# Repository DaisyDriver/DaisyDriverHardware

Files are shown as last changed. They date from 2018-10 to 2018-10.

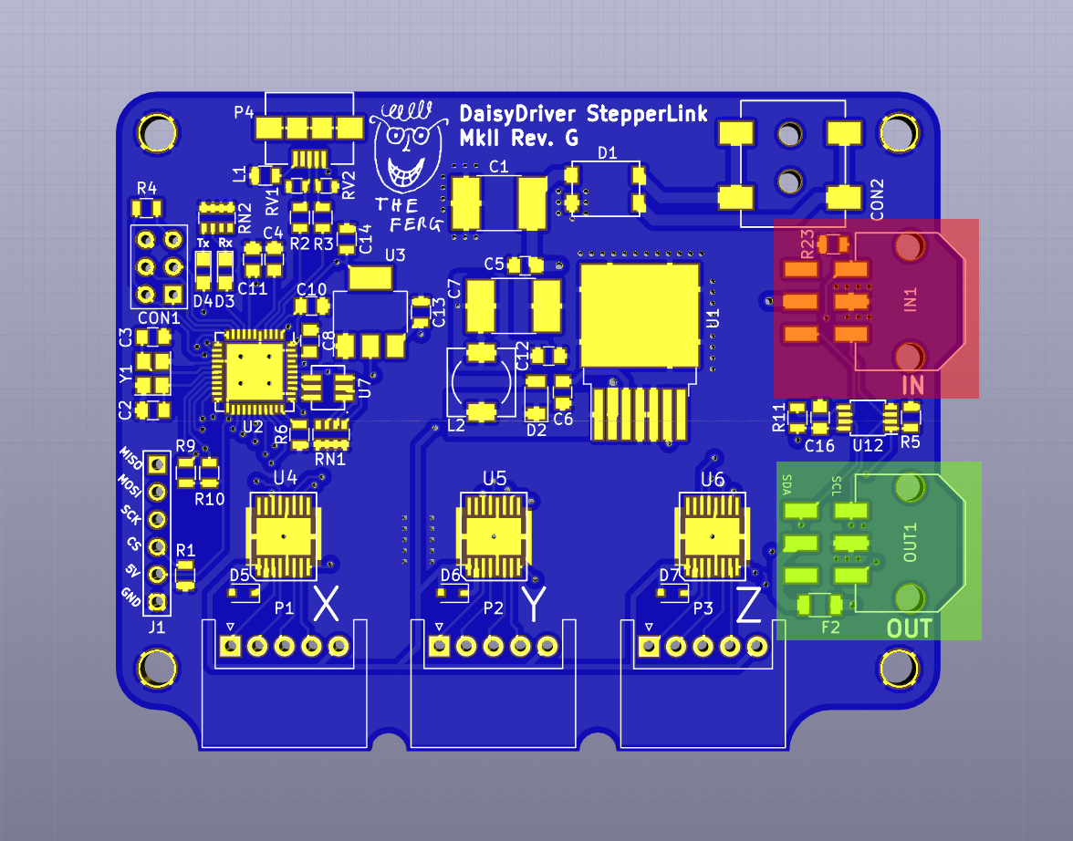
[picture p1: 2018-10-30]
board features/board_CAD_input_output.png

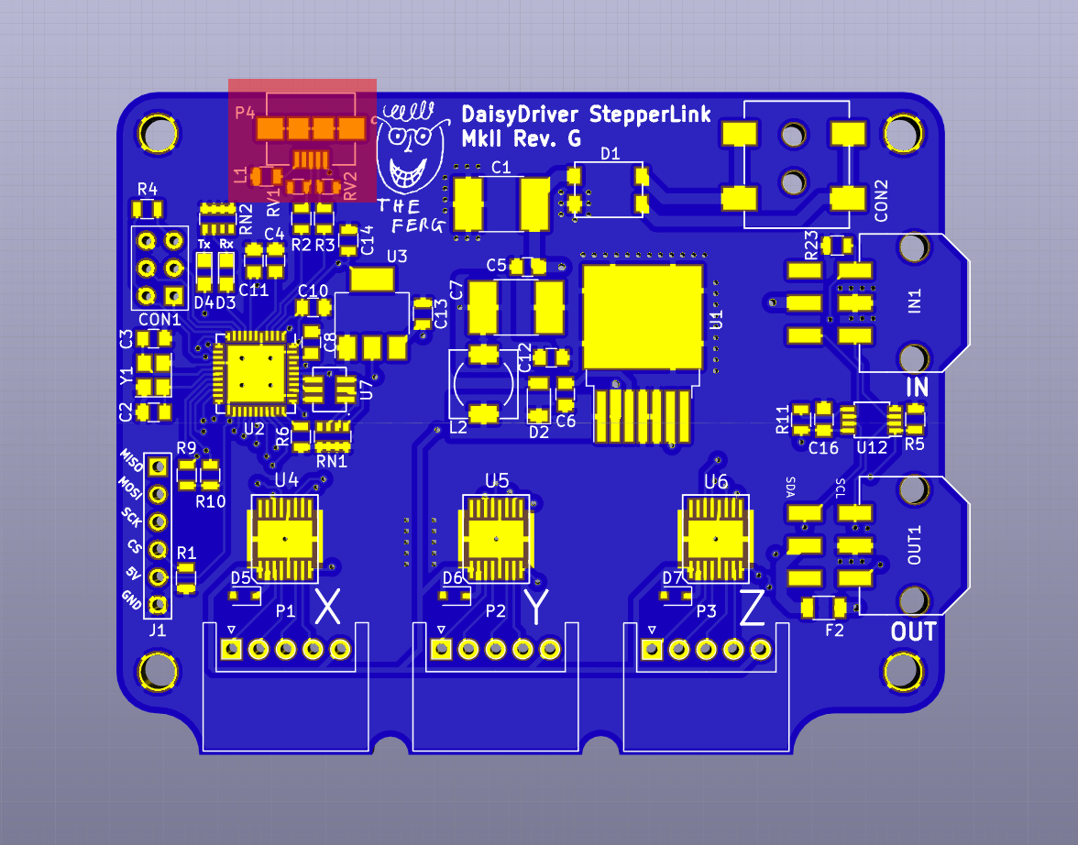
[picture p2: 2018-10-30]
board features/board_CAD_USB.png

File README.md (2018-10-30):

# DaisyDriver
The DaisyDriver project aims to make automation a common feature of scientific experiments by providing scientists with a simple, powerful interface to control motors in their setups. The [wiki](https://github.com/fr293/DaisyDriver/wiki/Getting-Started) contains information on how DaisyDrivers are assembled, programmed and operated.

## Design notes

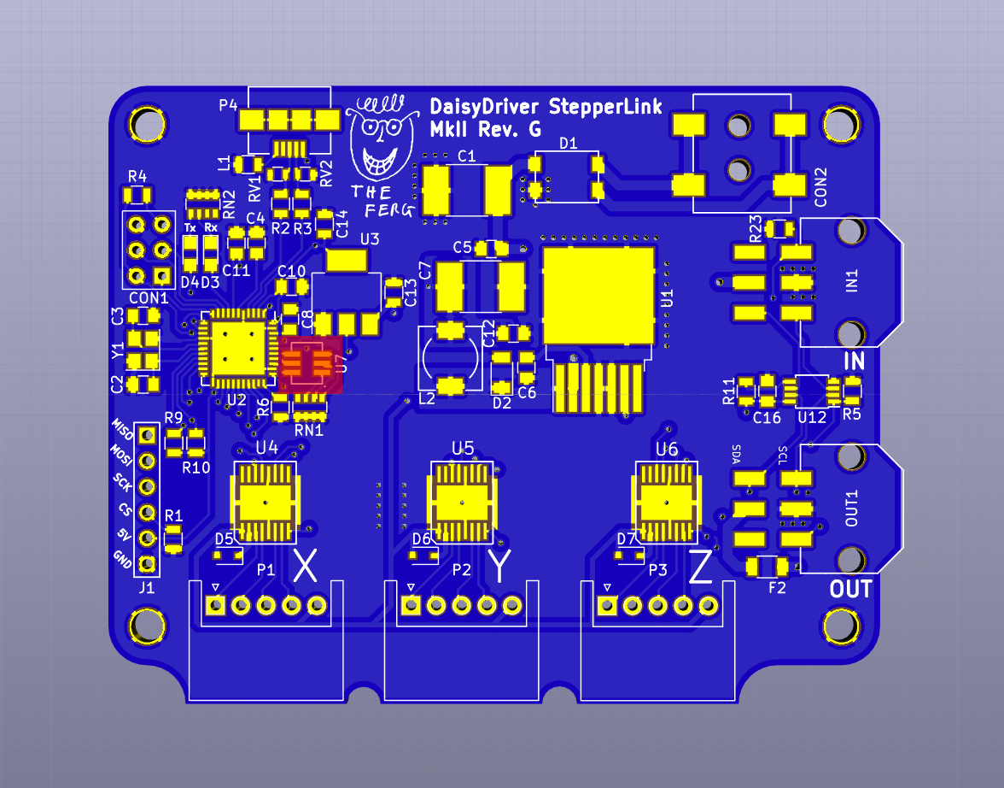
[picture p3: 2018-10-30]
board features/board_CAD_status_LED.png

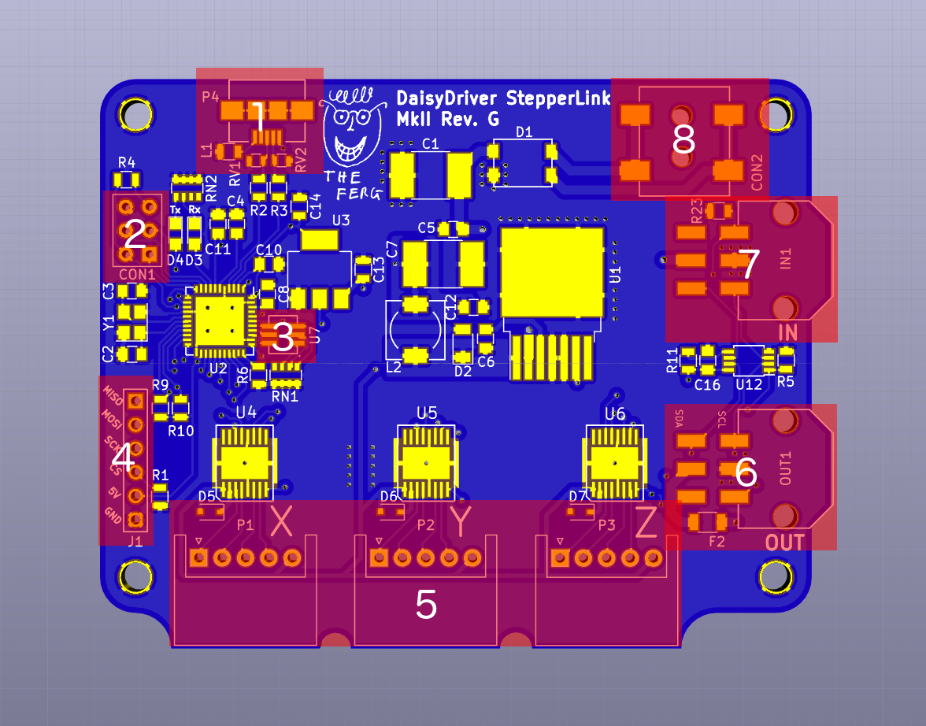
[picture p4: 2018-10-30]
board features/board_CAD_numbered_features.png

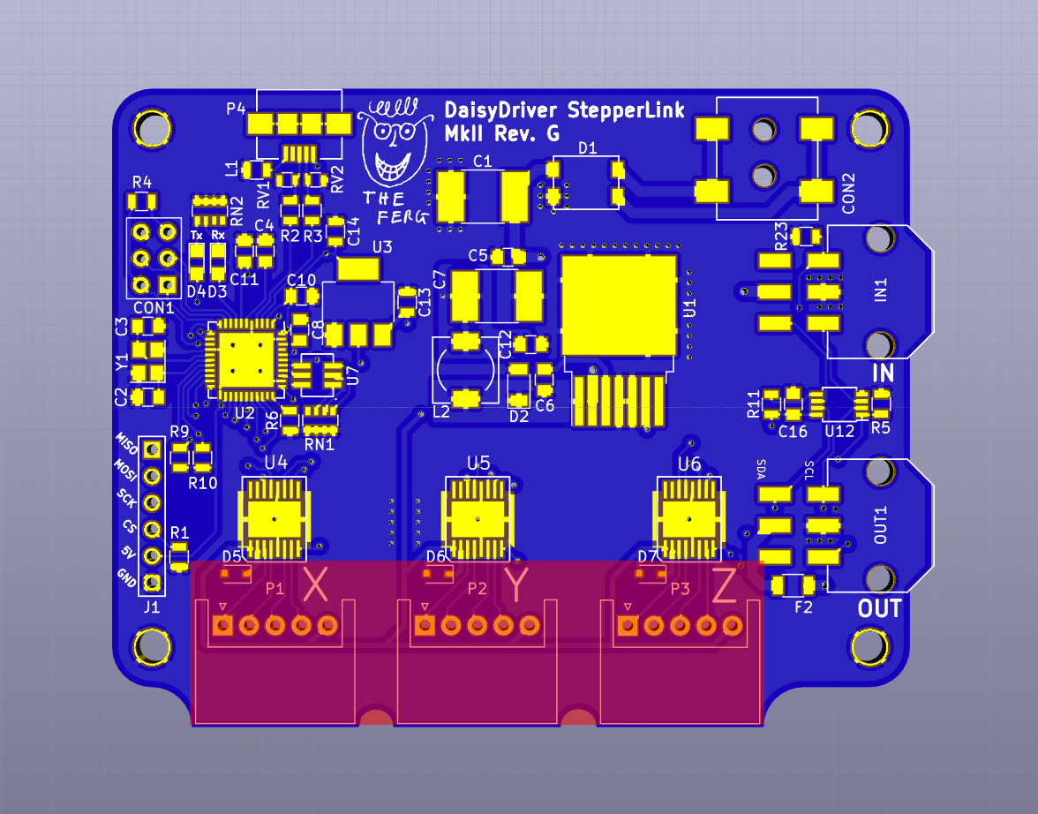
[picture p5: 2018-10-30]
board features/board_CAD_motors.png

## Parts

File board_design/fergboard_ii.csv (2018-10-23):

Id | Designator | Package | Quantity | Designation | Supplier and ref
1 | CON2 | SMD_Jack | 1 | BARREL_JACK
2 | L2 | Choke_SMD_6.3x6.3_H3 | 1 | 33u
3 | C2,C3 | C_0805 | 2 | 18p
4 | C4,C9,C12 | C_0805 | 3 | 1u
5 | C5,C10,C8,C11,C16 | C_0805 | 5 | 100n
6 | C6 | C_0805 | 1 | 10n
7 | CON1 | SW_NKK_G1xJP | 1 | AVR-ISP-6
8 | R2,R3 | R_0805 | 2 | 22
9 | R4,R9,R10,R23,R6,R11,R5,R13 | R_0805 | 8 | 10k
10 | RV2,RV1 | R_0603 | 2 | Varistor_[CG0603MLC-05E_Bourns]
11 | U2 | QFN-44-1EP_7x7mm_Pitch0.5mm | 1 | ATMEGA16U4-M-pad-connected
12 | U3 | SOT-223 | 1 | lm1117
13 | U4,U5,U6 | DRV8805 | 3 | DRV8805
14 | P4 | USB_Micro_B | 1 | USB_OTG
15 | Y1 | Crystal_SMD_3225-4pin_3.2x2.5mm | 1 | 16M_crystal
16 | F2 | R_1206 | 1 | 2A_Polyfuse
17 | F3,F4,F5 | R_1206 | 3 | 0A125_Polyfuse
18 | D2 | D_1206 | 1 | D_Schottky_0V7
19 | RN1 | R_Array_Convex_4x0603 | 1 | 1k
20 | C1 | R_2816 | 1 | 33u
21 | C7 | R_2816 | 1 | 330u
22 | D3,D4 | LED_0805 | 2 | Yellow
23 | F1 | R_1206 | 1 | 0A5_Polyfuse
24 | R7,R8 | R_0805 | 2 | 150
25 | D1 | CD-HD2004 | 1 | D_Bridge_+-AA
26 | U7 | RGB_LED | 1 | RGB_LED
27 | L1 | R_0805 | 1 | Ferrite_Bead
28 | D5,D6,D7 | D_SOD-323 | 3 | D_Zener
29 | C13 | R_2816 | 1 | 100u
30 | IN1,OUT1 | molex_micro_fit_3_by_2_right_angle | 2 | Molex_micro_fit_3*2
31 | U8,U9,U10,U11 | 3.1_hole | 4 | hole
32 | U1 | TO-263-7_TabPin8 | 1 | lm2676_TO-263
33 | C14 | R_0805 | 1 | 10u
34 | R1 | R_0805 | 1 | 1r
35 | U12 | TSSOP-8_4.4x3mm_Pitch0.65mm | 1 | PCA9511A
36 | U13 | ferg_graphic | 1 | ferg_logo
37 | U14 | SOT-553 | 1 | NL17SZ126
38 | P1,P2,P3 | JST_XH_S05B-XH-A_05x2.50mm_Angled | 3 | CONN_01X05
39 | R12 | R_0805 | 1 | 0R

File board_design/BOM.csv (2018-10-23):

Part Number | Quantity | Description | Number of unique parts
197671 | 10 | C1 | 37
1759194 | 10 | C2
1759194 | 10 | C3
2094043 | 10 | C4
7569564 | 10 | C5
2581081 | 10 | C6
2728631 | 10 | C7
7569564 | 10 | C8
1845748 | 10 | C9
7569564 | 10 | C10
7569564 | 10 | C11
1845748 | 10 | C12
2321230 | 10 | C13
2547035 | 10 | C14
7569564 | 10 | C16
1889309 | 10 | CON2
2676044 | 10 | D1
2400198 | 10 | D2
2099227 | 10 | D3
2099227 | 10 | D4
1431198 | 10 | D5
1431198 | 10 | D6
1431198 | 10 | D7
1596993 | 10 | F1
1596993 | 10 | F2
1596988 | 10 | F3
1596988 | 10 | F4
1596988 | 10 | F5
2781934 | 10 | IN1
1669753 | 10 | L1
2667912 | 10 | L2
2781934 | 10 | OUT1
1516293 | 10 | P1
1516293 | 10 | P2
1516293 | 10 | P3
2554978 | 10 | P4
2616757 | 10 | R1
1652962 | 10 | R2
1652962 | 10 | R3
2502671 | 10 | R5
2502671 | 10 | R4
2502671 | 10 | R6
1469877 | 10 | R7
1469877 | 10 | R8
2502671 | 10 | R9
2502671 | 10 | R10
2502671 | 10 | R11
2668292 | 10 | R12
2502671 | 10 | R13
2502671 | 10 | R23
2060100 | 10 | RN1
2060166 | 10 | RV1
1838966 | 10 | RV2
1469212 | 10 | U1
2425127 | 10 | U2
2323581 | 10 | U3
2099903 | 10 | U4
2099903 | 10 | U5
2099903 | 10 | U6
2368161 | 10 | U7
2212059 | 10 | U12
2342399 | 10 | U14
1611819 | 10 | Y1
2723776 | 10 | Cables
149968 | 1 | Solder paste

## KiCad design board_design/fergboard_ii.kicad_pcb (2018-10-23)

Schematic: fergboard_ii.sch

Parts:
C1: 33u; R_2816
C2, C3: 18p; C_0805
C4, C12: 1u; C_0805
C5, C8, C10, C11, C16: 100n; C_0805
C6: 10n; C_0805
C7: 330u; R_2816
C13, C14: 10u; R_0805
CON1: AVR-ISP-6; SW_NKK_G1xJP
CON2: BARREL_JACK; SMD_Jack
D1: D_Bridge_+-AA; CD-HD2004
D2: D_Schottky_0V7; D_1206
D3, D4: Yellow; LED_0805
D5, D6, D7: D_Zener; D_SOD-323
F2: 2A_Polyfuse; R_1206
IN1: Molex_micro_fit_3*2; molex_micro_fit_3_by_2_right_angle
J1: Conn_01x06; 1by6_connector
L1: Ferrite_Bead; R_0805
L2: 33u; Choke_SMD_6.3x6.3_H3
OUT1: Molex_micro_fit_3*2; molex_micro_fit_3_by_2_right_angle
P1, P2, P3: CONN_01X05; JST_XH_S05B-XH-A_05x2.50mm_Angled
P4: USB_OTG; USB_Micro_B
R1, R4, R5, R6, R9, R10, R11, R23: 10k; R_0805
R2, R3: 22; R_0805
RN1, RN2: 4k7; R_Array_Convex_4x0603
RV1, RV2: Varistor_[CG0603MLC-05E_Bourns]; R_0603
U1: lm2676_TO-263; TO-263-7_TabPin8
U2: ATMEGA16U4-M-pad-connected; QFN-44-1EP_7x7mm_Pitch0.5mm
U3: lm1117; SOT-223
U4, U5, U6: DRV8805
U7: RGB_LED
U8, U9, U10, U11: hole; 3.1_hole
U12: PCA9511A; TSSOP-8_3x3mm_Pitch0.65mm
U13: ferg_logo; LOGO
Y1: 16M_crystal; Crystal_SMD_3225-4pin_3.2x2.5mm

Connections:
1W_in: IN1.1 (Power_(misc)), R23.2, U2.40 ((ADC1)PF1)
1W_out: OUT1.3 (Misc_(Power)), U2.39 ((ADC4/TCK)PF4)
BLUE: U2.36 ((ADC7/TDI)PF7), U7.6 (BLUE_A)
CATCH_DIODE: C6.1, D2.1, L2.1, U1.1 (switch_output)
CONNECT_INPUTS: R5.2, U2.28 ((ADC11/PCINT4)PB4), U12.1
CS: J1.4, R1.2, U2.21 ((TXD/INT3)PD3)
D+: P4.3 (D+), R2.1, RV1.1
D-: P4.2 (D-), R3.1, RV2.1
DIRX: U2.12 ((OC0A/OC1C/~RTS~/PCINT7)PB7), U4.13 (DIR)
DIRY: U2.26 ((T1/~OC4D~/ADC9)PD6), U5.13 (DIR)
DIRZ: U2.27 ((T0/OC4D/ADC10)PD7), U6.13 (DIR)
ENABLE_MOTORS: U2.20 ((RXD/INT2)PD2), U4.8 (nENBL), U5.8 (nENBL), U6.8 (nENBL)
GREEN: U2.37 ((ADC6/TDO)PF6), U7.5 (GREEN_A)
MCU_POWER: C10.1, C14.1, C16.2, CON1.6, J1.5, R4.2, R9.2, R10.2, R11.1, U2.2 (UVCC), U2.14 (VCC), U2.24 (AVCC), U2.34 (VCC), U2.44 (AVCC), U3.2 (OUTPUT), U3.4 (OUTPUT), U12.8
MID_POWER_12V: C7.1, C12.1, C13.2, D5.2, D6.2, D7.2, L2.2, P1.5, P2.5, P3.5, U1.6 (FB), U3.3 (INPUT), U4.1 (VM), U5.1 (VM), U6.1 (VM)
MISO: CON1.1, J1.1, U2.11 ((PDO/MISO/PCINT3)PB3)
MOSI: CON1.5, J1.2, U2.10 ((PDI/MOSI/PCINT2)PB2)
unnamed: C2.1, U2.17 (XTAL1), Y1.1
unnamed: C3.1, U2.16 (XTAL2), Y1.3
unnamed: C4.1, U2.6 (UCAP)
unnamed: C6.2, U1.3 (CB)
unnamed: C8.1, U2.42 (AREF)
unnamed: CON2.1, D1.3
unnamed: CON2.2, CON2.3, D1.4
unnamed: D3.1, RN2.2
unnamed: D4.1, RN2.1
unnamed: D5.1, U4.2 (VCLAMP)
unnamed: D6.1, U5.2 (VCLAMP)
unnamed: D7.1, U6.2 (VCLAMP)
unnamed: F2.1, OUT1.5 (SCL)
unnamed: L1.1, P4.5 (GND)
unnamed: P1.1, U4.3 (OUT1)
unnamed: P1.2, U4.4 (OUT2)
unnamed: P1.3, U4.6 (OUT3)
unnamed: P1.4, U4.7 (OUT4)
unnamed: P2.1, U5.3 (OUT1)
unnamed: P2.2, U5.4 (OUT2)
unnamed: P2.3, U5.6 (OUT3)
unnamed: P2.4, U5.7 (OUT4)
unnamed: P3.1, U6.3 (OUT1)
unnamed: P3.2, U6.4 (OUT2)
unnamed: P3.3, U6.6 (OUT3)
unnamed: P3.4, U6.7 (OUT4)
unnamed: R2.2, U2.4 (D+)
unnamed: R3.2, U2.3 (D-)
unnamed: R6.2, U2.33 ((~HWB~)PE2)
unnamed: R11.2, U12.5
unnamed: RN1.1, U7.3 (RED_C)
unnamed: RN1.2, U7.2 (GREEN_C)
unnamed: RN1.3, U7.1 (BLUE_C)
POWER_IN_24V: C1.1, C5.1, D1.1 (+), F2.2, IN1.5 (SCL), U1.2 (Input)
RED: U2.38 ((ADC5/TMS)PF5), U7.4 (RED_A)
RST: CON1.3, R4.1, U2.13 (~RESET~)
RXLED: D3.2, U2.8 ((SS/PCINT0)PB0)
SCK: CON1.2, J1.3, U2.9 ((SCLK/PCINT1)PB1)
SCL: OUT1.1 (Power_(misc)), R9.1, U2.18 ((OC0B/SCL/INT0)PD0), U12.2
SCL_IN: IN1.3 (Misc_(Power)), U12.3
SDA: OUT1.4 (SDA_(1-wire)), R10.1, U2.19 ((SDA/INT1)PD1), U12.7
SDA_IN: IN1.6 (1-wire_(SDA)), U12.6
SM0: U2.30 ((ADC13/OC1B/OC4B/PCINT13)PB6), U4.11 (SM0), U5.11 (SM0), U6.11 (SM0)
SM1: U2.29 ((ADC12/OC1A/~OC4B~/PCINT12)PB5), U4.10 (SM1), U5.10 (SM1), U6.10 (SM1)
STEPX: U2.31 ((OC3A/~OC4A~)PC6), U4.14 (STEP)
STEPY: U2.25 ((ICP2/ADC8)PD4), U5.14 (STEP)
STEPZ: U2.1 ((INT6/AIN0)PE6), U6.14 (STEP)
TXLED: D4.2, U2.22 ((XCK1/~CTS~)PD5)
VBUS: C11.1, P4.1 (VBUS), U2.7 (VBUS)

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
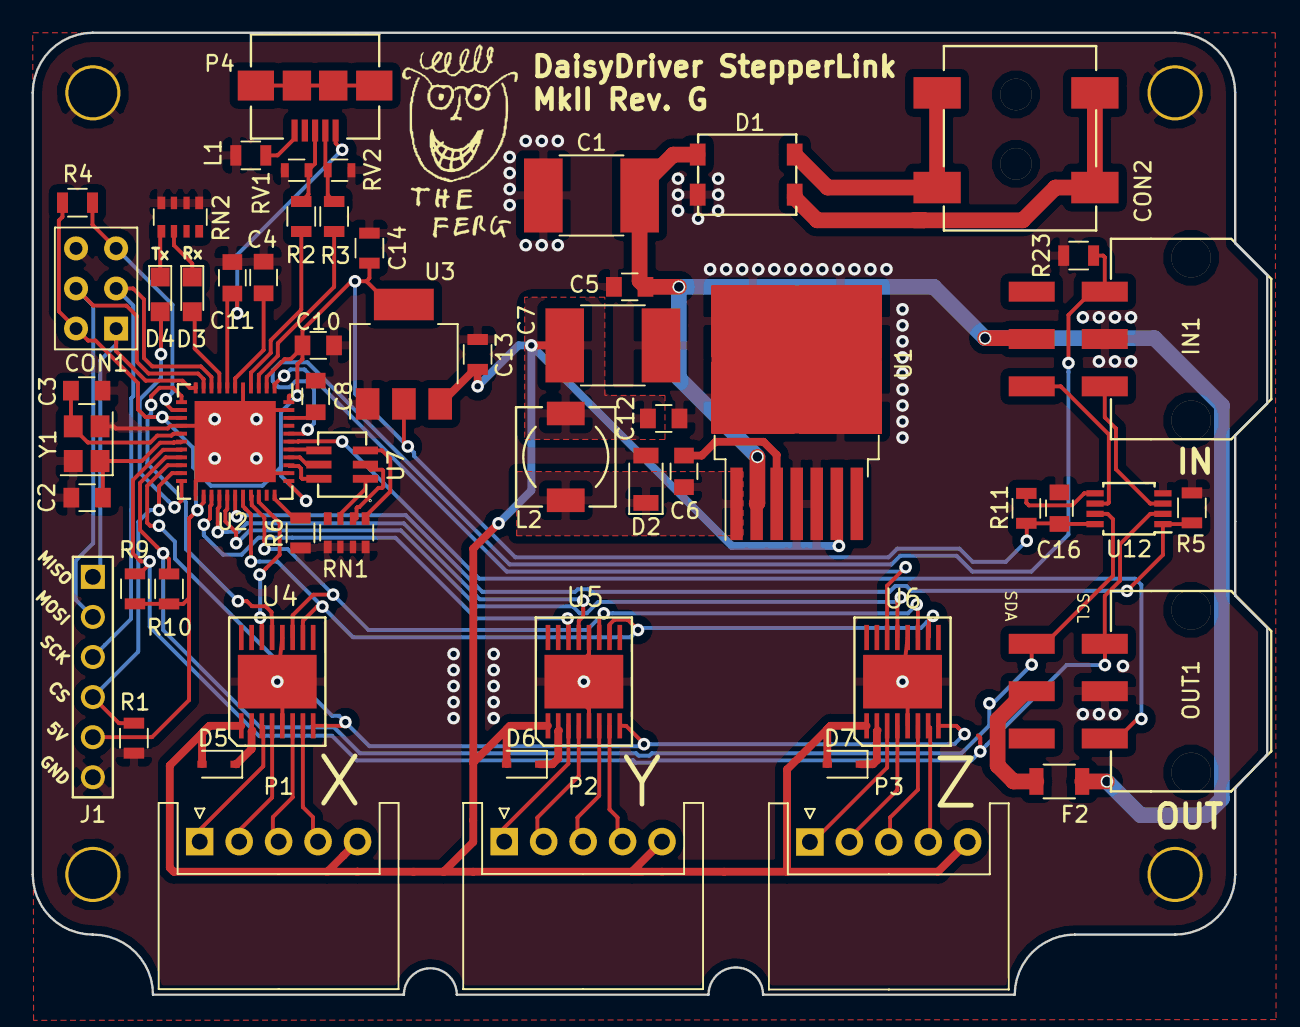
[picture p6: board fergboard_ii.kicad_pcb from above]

Board: 2 copper layers, 78.2 x 61.0 mm, 61 parts (0 on the bottom side), 67 nets.

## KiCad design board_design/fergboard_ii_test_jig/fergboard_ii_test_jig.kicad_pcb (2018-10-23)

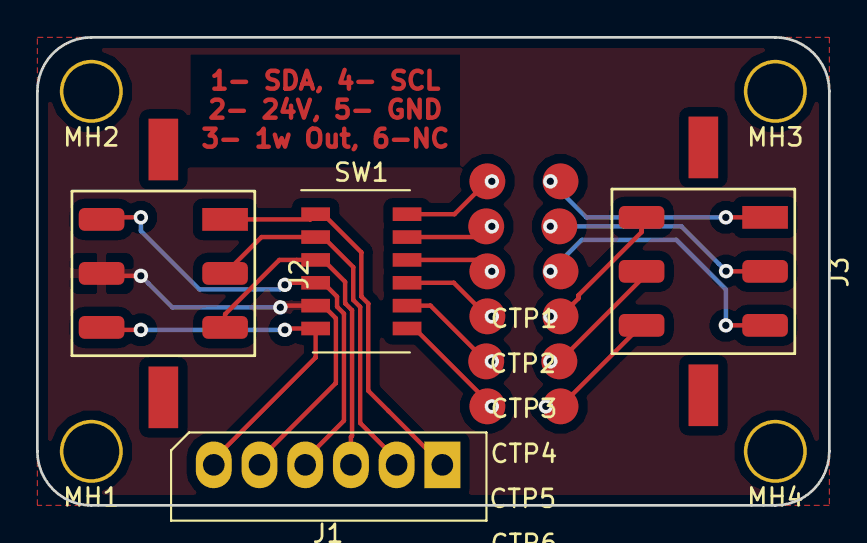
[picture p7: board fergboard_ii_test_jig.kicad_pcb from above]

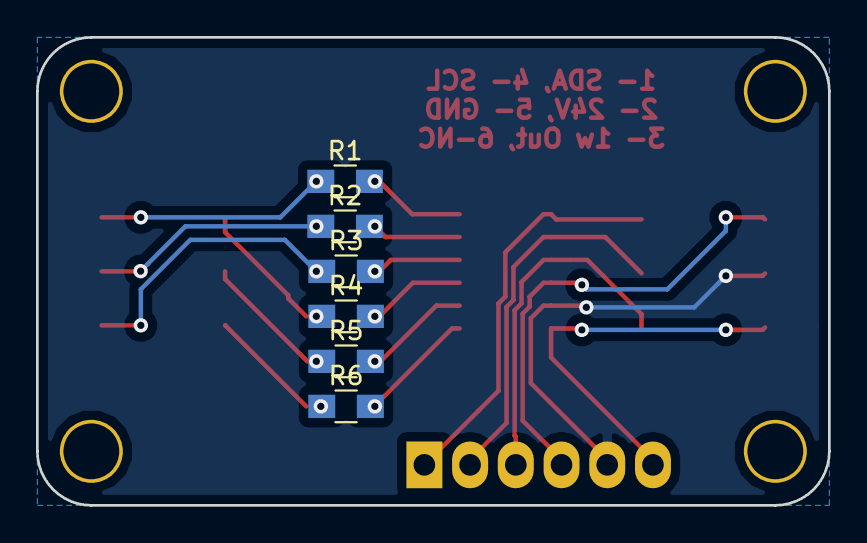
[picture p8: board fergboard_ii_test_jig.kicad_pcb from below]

Board: 2 copper layers, 44.0 x 26.0 mm, 20 parts (6 on the bottom side), 18 nets.

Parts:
CTP1, CTP2, CTP3, CTP4, CTP5, CTP6: current_test; Current_test_point
J1: Conn_01x06_Male; Molex_SPOX-5267_22-03-5065_06x2.54mm_Straight
J2, J3: molex_micro_fit_3*2; molex_microfit_3_by_2
MH1, MH2, MH3, MH4: MountingHole_Pad; 3.1_hole
R1, R2, R3, R4, R5, R6: 1R; R_0805_HandSoldering
SW1: SW_DIP_x06; SW_DIP_x6_W5.08mm_Slide_Copal_CHS-A

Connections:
HI_1: CTP1.1, R1.2, SW1.12
HI_2: CTP2.1, R2.2, SW1.11
HI_3: CTP3.1, R3.2, SW1.10
HI_4: CTP4.1, R4.2, SW1.9
HI_5: CTP5.1, R5.2, SW1.8
HI_6: CTP6.1, R6.2, SW1.7
IN_1: J1.1, J2.1, SW1.1
IN_2: J1.2, J2.2, SW1.2
IN_3: J1.3, J2.3, SW1.3
IN_4: J1.4, J2.4, SW1.4
IN_5: J1.5, J2.5, SW1.5
IN_6: J1.6, J2.6, SW1.6
OUT_1: CTP1.2, J3.1, R1.1
OUT_2: CTP2.2, J3.2, R2.1
OUT_3: CTP3.2, J3.3, R3.1
OUT_4: CTP4.2, J3.4, R4.1
OUT_5: CTP5.2, J3.5, R5.1
OUT_6: CTP6.2, J3.6, R6.1

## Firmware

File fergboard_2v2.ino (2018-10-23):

/*
  pin assignments:
  D0- enbl_x
  D1- dir_y
  D2- scl
  D3- sda
  D4- stp_y
  D5- stp_x
  D6- dir_z
  D7- stp_z
  D8- enbl_c
  D9- sm1
  D10- sm0
  D11- dir_x
  D12- enbl_y
  D13- NO ASSIGNMENT
  D14- NO ASSIGNMENT
  D15- NO ASSIGNMENT
  D16- NO ASSIGNMENT
  A0- blue
  A1- green
  A2- red
  A3- 1w_out
  A4- 1w_in
  A5- enbl_z

  chip settings:
  SM0, SM1 - setting
  0, 0 - full step
  0, 1 - half step
  1, 0 - wave drive (quarter step)
  1, 1 - not allowed
*/

//libraries required
#include <Wire.h>
#include <SerialCommandFergboard.h>

//pin definitions
#define enbl_x 0
#define dir_y 1
#define stp_y 4
#define stp_x 5
#define dir_z 6
#define stp_z 7
#define enbl_c 8
#define sm1 9
#define sm0 10
#define dir_x 11
#define enbl_y 12
#define blue A0
#define green A1
#define red A2
#define ow_out A3
#define ow_in A4
#define enbl_z A5

//declare global variables
//speed is measured in steps/s

int x_speed = 500;
int y_speed = 500;
int z_speed = 500;

long x_period = 1000000/x_speed;
long y_period = 1000000/y_speed;
long z_period = 1000000/z_speed;

long x_pos = 0;
long y_pos = 0;
long z_pos = 0;

SerialCommand sCmd;

volatile bool twiFlag = false;
char *twiPointer;

void setup() {
  // set the pins correctly for their modes of operation
  pinMode(enbl_x, OUTPUT);
  pinMode(dir_y, OUTPUT);
  pinMode(stp_y, OUTPUT);
  pinMode(stp_x, OUTPUT);
  pinMode(dir_z, OUTPUT);
  pinMode(stp_z, OUTPUT);
  pinMode(enbl_c, OUTPUT);
  pinMode(sm1, OUTPUT);
  pinMode(sm0, OUTPUT);
  pinMode(dir_x, OUTPUT);
  pinMode(enbl_y, OUTPUT);
  pinMode(blue, OUTPUT);
  pinMode(green, OUTPUT);
  pinMode(red, OUTPUT);
  pinMode(ow_out, OUTPUT);
  pinMode(ow_in, INPUT);
  pinMode(enbl_z, OUTPUT);
  USBCON |= (1 << OTGPADE);

  // read and write all the pins to set them up correctly

  //set up the motors
  digitalWrite(enbl_x, HIGH);
  digitalWrite(dir_x, LOW);
  digitalWrite(stp_x, LOW);

  digitalWrite(enbl_y, HIGH);
  digitalWrite(dir_y, LOW);
  digitalWrite(stp_y, LOW);

  digitalWrite(enbl_z, HIGH);
  digitalWrite(dir_z, LOW);
  digitalWrite(stp_z, LOW);

  //set up the one wire interface
  digitalWrite(ow_out, LOW);
  digitalRead(ow_in);

  //set up the motors for half stepping
  digitalWrite(sm1, HIGH);
  digitalWrite(sm0, LOW);

  int address = oneWire();

  Serial.begin(115200);
  
  Wire.onReceive(receiveEvent); // register event
  Wire.onRequest(requestEvent);


  //set up the serial commands
  sCmd.addCommand("NET", network);
  sCmd.addCommand("LON", lightOn);
  sCmd.addCommand("LOF", lightOff);
  sCmd.addCommand("TST", test);
  sCmd.addCommand("STV", setVelocity);
  sCmd.addCommand("MOV", moveStage);
  sCmd.addCommand("JOG", jogStage); 
  sCmd.addCommand("POS", reportPosition);
  sCmd.addCommand("PTH", path); 
  sCmd.addCommand("SLP", sleep); 
  sCmd.addCommand("ENG", energise);
  sCmd.addCommand("STM", steppingMode);
  sCmd.addCommand("RSM", resetMotors);
  sCmd.addCommand("ERR", error);
  
  sCmd.addDefaultHandler(unrecognised);  // Handler for command that isn't matched

  //show that the board is operational
  longPulse(red, 1);
  longPulse(green, 1);
  longPulse(blue, 1);
  longPulse(green, address);
  //digitalWrite(green, HIGH);
  Serial.print("Ready\n");
}


void loop() {
  // this checks the serial queue for commands and executes them
  sCmd.readSerial();
  if(twiFlag){
    digitalWrite(green, HIGH);
    sCmd.addBufferMod(twiPointer);
    twiFlag = false;
    digitalWrite(green, LOW);
  }
}

void receiveEvent() {
  volatile char twiBuffer[32];
  volatile char *wireChar;
  volatile int i = 0;
  while (Wire.available()) { 
    twiBuffer[i] = Wire.read();
    i++;
  }
  twiBuffer[i] = NULL;
 
//  wireChar = Wire.read();
//  strcpy(twiBuffer,wireChar);
//
//  while( Wire.available()) {
//    wireChar = Wire.read();
//    strcat(twiBuffer,wireChar);
//  }
  
  twiPointer = twiBuffer;
  twiFlag = true;
}

void requestEvent() {
  char buf [4] = { '1', '2', '3', '4' };
  Wire.write (buf, sizeof buf);  
}

void longPulse(int pin, int num) {
  for (int i = 0; i < num; i++) {
    digitalWrite(pin, HIGH);
    delay (200);
    digitalWrite(pin, LOW);
    delay (200);
  }
}

void lightOn(){
  digitalWrite(red, HIGH);
}

void lightOff(){
  digitalWrite(red, LOW);
}

void pulse(int pin) {
    digitalWrite(pin, HIGH);
    delayMicroseconds(2);
    digitalWrite(pin, LOW);
}

void test(){
    //char command[] = {'M', 'O', 'V', ' ', '5', '0', '0',' ', '5', '0', '0',' ', '5', '0', '0', '\r'};
   // char *string = command;
    //sCmd.addBufferMod(command);
    longPulse(blue,4);
}

void network(){
  int board;
  char *wirecommand;
  char commandstring[32];
  char *commandstringref;
  board = atoi(sCmd.next());
  wirecommand = sCmd.next();
  strcpy(commandstring, wirecommand);

  if(board == 1){
    // load into own buffer
     while(wirecommand != NULL){
      wirecommand = sCmd.next();
      strcat(commandstring, " ");
      strcat(commandstring, wirecommand);
     }
     strcat(commandstring, "\r");
     commandstringref = commandstring;
     sCmd.addBufferMod(commandstringref);  
  }
  else{
    // send over wire
    Wire.beginTransmission(board);
     while(wirecommand != NULL){
      Wire.write(wirecommand);
      Wire.write(" ");
      wirecommand = sCmd.next();
     }
     Wire.write("\r");
     Wire.endTransmission();
  }
}

void setVelocity(){

  x_speed = atoi(sCmd.next());
  y_speed = atoi(sCmd.next());
  z_speed = atoi(sCmd.next());

  x_period = 1000000/x_speed;
  y_period = 1000000/y_speed;
  z_period = 1000000/z_speed;
  
}

void moveStage(){
   //this may require alteration to deal with different stepping modes
  char *arg;
 
  long x_count = 0;
  long y_count = 0;
  long z_count = 0;
  long x_target = 0;
  long y_target = 0;
  long z_target = 0;

// read in the arguments and cast them as ints
  x_target = atoi(sCmd.next());
  y_target = atoi(sCmd.next());
  z_target = atoi(sCmd.next());

  x_count = x_target - x_pos;
  y_count = y_target - y_pos;
  z_count = z_target - z_pos;

  x_pos = x_target;
  y_pos = y_target;
  z_pos = z_target;

  
// set the direction lines according to the polarity of the arguments
  if (x_count < 0){
    x_count = abs(x_count);
    digitalWrite(dir_x,HIGH);
  }
  else{
    digitalWrite(dir_x,LOW);
  }

  if (y_count < 0){
    y_count = abs(y_count);
    digitalWrite(dir_y,HIGH);
  }
    else{
    digitalWrite(dir_y,LOW);
  }

  if (z_count < 0){
    z_count = abs(z_count);
    digitalWrite(dir_z,HIGH);
  }
    else{
    digitalWrite(dir_z,LOW);
  }


digitalWrite(enbl_x, LOW);
digitalWrite(enbl_y, LOW);
digitalWrite(enbl_z, LOW);

long xtest = micros();
long ytest = micros();
long ztest = micros();

long xtestadj = 0;
long ytestadj = 0;
long ztestadj = 0;

long donetime = micros();

long x_timer = micros();
long y_timer = micros();
long z_timer = micros();

long xerror = 0;
long yerror = 0;
long zerror = 0;



while(x_count > 0 || y_count > 0 || z_count > 0){

  if(x_count > 0){
    xtest = (micros() - x_timer);
    if(xtest > x_period - xtestadj){
        x_timer = micros();
        xerror = xerror + (xtest - x_period);
        xtestadj = xtestadj + (xtest - x_period) + 6;
        pulse(stp_x);
        x_count -- ;
    }
  }

  if(y_count > 0){
   ytest = (micros() - y_timer);
    if(ytest > y_period - ytestadj){
        y_timer = micros();
        yerror = yerror + (ytest - y_period);
        ytestadj = ytestadj + (ytest - y_period) + 6;
        pulse(stp_y);
        y_count -- ;
    }
  }

  if(z_count > 0){
    ztest = (micros() - z_timer);
    if(ztest > z_period - ztestadj){
        z_timer = micros();
        zerror = zerror + (ztest - z_period);
        ztestadj = ztestadj + (ztest - z_period) + 6;
        pulse(stp_z);
        z_count -- ;
    }
  }

}

donetime = micros() - donetime;

digitalWrite(enbl_x, HIGH);
digitalWrite(enbl_y, HIGH);
digitalWrite(enbl_z, HIGH);

Serial.print("Done Moving in ");

float floattime = donetime/1000000.0;

Serial.print(floattime,6);

Serial.print(" seconds\n");

}

void jogStage(){
  digitalWrite(green, LOW);
  digitalWrite(blue, HIGH);
  //this may require alteration to deal with different stepping modes
  char *arg;
  int x_flag = 0;
  int y_flag = 0;
  int z_flag = 0;
  long x_count = 50;
  long y_count = 50;
  long z_count = 50;

// read in the arguments and cast them as ints
  x_flag = atoi(sCmd.next());
  y_flag = atoi(sCmd.next());
  z_flag = atoi(sCmd.next());

// set the direction lines according to the polarity of the arguments
  if (x_flag == -1){
    digitalWrite(dir_x,HIGH);
  }
  else if (x_flag == 1){
    digitalWrite(dir_x,LOW);
  }
  else{
    x_count = 0;
  }

  if (y_flag == -1){
    digitalWrite(dir_y,HIGH);
  }
  else if (y_flag == 1){
    digitalWrite(dir_y,LOW);
  }
  else{
    y_count = 0;
  }

  if (z_flag == -1){
    digitalWrite(dir_z,HIGH);
  }
  else if (z_flag == 1){
    digitalWrite(dir_z,LOW);
  }
  else{
    z_count = 0;
  }

digitalWrite(enbl_x, LOW);
digitalWrite(enbl_y, LOW);
digitalWrite(enbl_z, LOW);

long xtest = micros();
long ytest = micros();
long ztest = micros();

long xtestadj = 0;
long ytestadj = 0;
long ztestadj = 0;

long donetime = micros();

long x_timer = micros();
long y_timer = micros();
long z_timer = micros();

long xerror = 0;
long yerror = 0;
long zerror = 0;

while(x_count > 0 || y_count > 0 || z_count > 0){

  if(x_count > 0){
    xtest = (micros() - x_timer);
    if(xtest > x_period - xtestadj){
        x_timer = micros();
        xerror = xerror + (xtest - x_period);
        xtestadj = xtestadj + (xtest - x_period) + 6;
        pulse(stp_x);
        x_count -- ;
    }
  }

  if(y_count > 0){
   ytest = (micros() - y_timer);
    if(ytest > y_period - ytestadj){
        y_timer = micros();
        yerror = yerror + (ytest - y_period);
        ytestadj = ytestadj + (ytest - y_period) + 6;
        pulse(stp_y);
        y_count -- ;
    }
  }

  if(z_count > 0){
    ztest = (micros() - z_timer);
    if(ztest > z_period - ztestadj){
        z_timer = micros();
        zerror = zerror + (ztest - z_period);
        ztestadj = ztestadj + (ztest - z_period) + 6;
        pulse(stp_z);
        z_count -- ;
    }
  }

}

donetime = micros() - donetime;

digitalWrite(enbl_x, HIGH);
digitalWrite(enbl_y, HIGH);
digitalWrite(enbl_z, HIGH);

Serial.println("FIN");

digitalWrite(blue, LOW);
digitalWrite(green, HIGH);
}

void reportPosition(){
  Serial.print(x_pos);
  Serial.print(" ");
  Serial.print(y_pos);
  Serial.print(" ");
  Serial.println(z_pos);
}

void path(){
 char *arg;

   
}

void sleep(){
  char *arg;

}

void energise(){
 
digitalWrite(enbl_x, LOW);
digitalWrite(enbl_y, LOW);
digitalWrite(enbl_z, LOW);
}

void steppingMode(){
  char *arg;

}

void resetMotors(){
 char *arg;

}

void error(){
  char *arg;

}

int oneWire(){
  int address = 1;
  bool middle = false;
  bool wait = true;

  digitalWrite(enbl_c,HIGH);
              
  if(USBSTA&(1<<VBUS)){
    Wire.begin(address);
      delay(100);
    digitalWrite(ow_out, HIGH);
            }

  else{
    Wire.begin();
    digitalWrite(red,HIGH);
    delay(100);
    while(wait){
      wait = digitalRead(ow_in);
      delay(100);
                }
    digitalWrite(red,LOW);
    delay(100);
                
       address = sweeper();
       Wire.begin(address);
       digitalWrite(ow_out, HIGH);
      }
  return address;
}

int sweeper() {
  int i = 2;
  int trans = 0;
  bool check = false;
  while(!check){
  Wire.beginTransmission(i);
  trans = Wire.endTransmission();
  if(trans == 2){
    check = true;
                }
  else{
   i++;               
      }
               }
         return i;
               }

void unrecognised()
{
  Serial.println("Command Not Recognised");
}

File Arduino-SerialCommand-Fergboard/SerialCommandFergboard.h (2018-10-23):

/******************************************************************************* 
SerialCommand - An Arduino library to tokenize and parse commands received over
a serial port. 
Copyright (C) 2011-2013 Steven Cogswell  <steven.cogswell@gmail.com>
http://awtfy.com

Version 20131021A.   

Version History:
May 11 2011 - Initial version
May 13 2011 -	Prevent overwriting bounds of SerialCommandCallback[] array in addCommand()
			defaultHandler() for non-matching commands
Mar 2012 - Some const char * changes to make compiler happier about deprecated warnings.  
           Arduino 1.0 compatibility (Arduino.h header) 
Oct 2013 - SerialCommand object can be created using a SoftwareSerial object, for SoftwareSerial
           support.  Requires #include <SoftwareSerial.h> in your sketch even if you don't use 
           a SoftwareSerial port in the project.  sigh.   See Example Sketch for usage. 
Oct 2013 - Conditional compilation for the SoftwareSerial support, in case you really, really
           hate it and want it removed.  

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
You should have received a copy of the GNU Lesser General Public
License along with this library; if not, write to the Free Software
Foundation, Inc., 51 Franklin Street, Fifth Floor, Boston, MA  02110-1301  USA
***********************************************************************************/
#ifndef SerialCommand_h
#define SerialCommand_h

#if defined(ARDUINO) && ARDUINO >= 100
#include "Arduino.h"
#else
#include "WProgram.h"
#endif

// If you want to use SerialCommand with the hardware serial port only, and want to disable
// SoftwareSerial support, and thus don't have to use "#include <SoftwareSerial.h>" in your
// sketches, then uncomment this define for SERIALCOMMAND_HARDWAREONLY, and comment out the 
// corresponding #undef line.  
//
// You don't have to use SoftwareSerial features if this is not defined, you can still only use 
// the Hardware serial port, just that this way lets you get out of having to include 
// the SoftwareSerial.h header. 
#define SERIALCOMMAND_HARDWAREONLY 1
//#undef SERIALCOMMAND_HARDWAREONLY

#ifdef SERIALCOMMAND_HARDWAREONLY
#warning "Warning: Building SerialCommand without SoftwareSerial Support"
#endif

#ifndef SERIALCOMMAND_HARDWAREONLY 
#include <SoftwareSerial.h>  
#endif

#include <string.h>


#define SERIALCOMMANDBUFFER 	32
#define MAXSERIALCOMMANDS		10
#define MAXDELIMETER 10

#define SERIALCOMMANDDEBUG 1
#undef SERIALCOMMANDDEBUG      // Comment this out to run the library in debug mode (verbose messages)
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
